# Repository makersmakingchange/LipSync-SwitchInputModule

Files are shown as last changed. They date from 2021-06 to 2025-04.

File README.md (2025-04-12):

# LipSync Switch Input Module

**As of 2024-Feb-08, this version of the LipSync is now obsolete and has been replaced by the [LipSync 4](https://github.com/makersmakingchange/LipSync).**
The LipSync 4 has 3 integrated switch ports for users who are unable to use sip and puff. Design files and documentation are maintained here for information only.

The LipSync Switch Input Module enables a user to use a [LipSync Classic](https://www.makersmakingchange.com/project/lipsync-classic/) with two assistive switches instead of the standard Sip and Puff mouthpiece. This can be a helpful adaptation for anyone who has difficulty forming their lips around the mouthpiece or generating the typical sips and puffs.

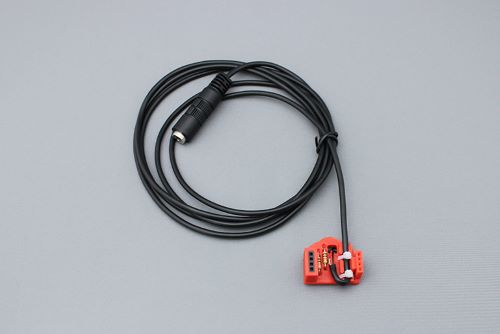
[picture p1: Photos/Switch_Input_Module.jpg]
LipSync Switch Input Module


## Getting Started

### 1. Order the Off-The-Shelf Components

The [Bill of Materials](/Documentation/Switch_Input_Module_BOM_v1.0.xlsx) lists all of the parts and components required to build the Switch Input Module. The electronic components may be available locally, but will probably need to be ordered online. Make sure you order the correct splitter.

### 2. Print the 3D Printed Circuit Board

Print the 3D Printed Circuit Board. The [file](/Build_Files/3D_Printing_Files/Switch_Input_3DPCB.stl) is in the [/Build_Files/3D_Printing_Files](/Build_Files/3D_Printing/) folder.

### 3. Disassemble the LipSync, Assemble and Install the Module, and Reassemble the LipSync 

Reference the [assembly guide](/Documentation/Switch_Input_Module_Assembly_Guide_v1.0.pdf) for the tools and steps required to complete each portion.

### 4. Attach an appropriate splitter and two suitable assistive switches.

Attach two momentary assistive switches.

## Files

### Documentation
| Document             | Version | Link                                                                                  |
|----------------------|---------|---------------------------------------------------------------------------------------|
| Design Rationale     | 1.0     | [Design_Rationale](/Documentation/Switch_Input_Module_Design_Rationale_v1.0.pdf) |
| Bill of Materials    | 1.0     | [BOM](/Documentation/Switch_Input_Module_BOM_v1.0.xlsx)                          |
| Assembly Guide       | 1.0     | [Assembly Guide](/Documentation/Switch_Input_Module_Assembly_Guide_v1.0.pdf)       |
| Quality Check Guide  | 1.0     | [Assembly Guide](/Documentation/Switch_Input_Module_Quality_Check_Guide_v1.0.pdf)       |
| User Quick Guide     | 1.0     | [Quick_Guide](/Documentation/Switch_Input_Module_User_Quick_Guide_v1.0.pdf)           |

### Design Files
 - [CAD Files](/Design_Files)

### Build Files
 - [3D Printing Files](/Build_Files/3D_Printing)
 - [V1.0 STL](/Build_Files/3D_Printing_Files/Switch_Input_3DPCB.stl)

## License
Copyright (c) 2022-2024 Neil Squire / Makers Making Change.

This repository describes Open Hardware:
 - Everything needed or used to design, make, test, or prepare the LipSync Switch Input Module is licensed under the [CERN 2.0 Weakly Reciprocal license (CERN-OHL-W v2) or later](https://cern.ch/cern-ohl ) .
 - Accompanying material such as instruction manuals, videos, and other copyrightable works that are useful but not necessary to design, make, test, or prepare the LipSync are published under a [Creative Commons Attribution-ShareAlike 4.0 license (CC BY-SA 4.0)](https://creativecommons.org/licenses/by-sa/4.0/) .

You may redistribute and modify this documentation and make products using it under the terms of the [CERN-OHL-W v2](https://cern.ch/cern-ohl).
This documentation is distributed WITHOUT ANY EXPRESS OR IMPLIED WARRANTY, INCLUDING OF MERCHANTABILITY, SATISFACTORY QUALITY AND FITNESS FOR A PARTICULAR PURPOSE.
Please see the CERN-OHL-W v2 for applicable conditions.

Source Location: https://github.com/makersmakingchange/LipSync-SwitchInputModule

## Attribution

The LipSync Switch Input Module was designed by Neil Squire Society / Makers Making Change. The initial development of a 3D printable LipSync was supported by the Google Impact Challenge: Disabilities grant from Google.org. Further development was supported through the Government of Canada's Innovation Science and Economic Development Assistive Technology Program. These and other funders have also enabled Neil Squire / Makers Making Change to deploy numerous LipSyncs to users at reduced cost.

### Contributors
Designers:
  - Derrick Andrews, Neil Squire Society / Makers Making Change.

----

<!-- ABOUT MMC START -->
## About Makers Making Change
[Makers Making Change Logo](https://www.makersmakingchange.com/)

Makers Making Change is a program of [Neil Squire](https://www.neilsquire.ca/), a Canadian non-profit that uses technology, knowledge, and passion to empower people with disabilities.

Makers Making Change leverages the capacity of community based Makers, Disability Professionals and Volunteers to develop and deliver affordable Open Source Assistive Technologies.

 - Website: [www.MakersMakingChange.com](https://www.makersmakingchange.com/)
 - GitHub: [makersmakingchange](https://github.com/makersmakingchange)
 - Bluesky: [@makersmakingchange.bsky.social](https://bsky.app/profile/makersmakingchange.bsky.social)
 - Instagram: [@makersmakingchange](https://www.instagram.com/makersmakingchange)
 - Facebook: [makersmakechange](https://www.facebook.com/makersmakechange)
 - LinkedIn: [Neil Squire Society](https://www.linkedin.com/company/neil-squire-society/)
 - Thingiverse: [makersmakingchange](https://www.thingiverse.com/makersmakingchange/about)
 - Printables: [MakersMakingChange](https://www.printables.com/@MakersMakingChange)

### Contact Us
For technical questions, to get involved, or to share your experience we encourage you to [visit our website](https://www.makersmakingchange.com/) or [contact us](https://www.makersmakingchange.com/s/contact).
<!-- ABOUT MMC END -->

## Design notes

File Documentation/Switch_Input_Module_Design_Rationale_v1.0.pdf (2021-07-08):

V1.0 | May 2021

## LipSync Switch Input Module

## Design Rationale

© 2021 by Neil Squire.
This work is licensed under the CC BY SA 4.0 License: http://creativecommons.org/licenses/by-sa/4.0
Files available at https://www.makersmakingchange.com/project/lipsync-switch-input-module/ | Page 1 of 7

## Introduction

The LipSync is a mouth operated joystick that emulates a computer mouse using a combination of lip movements and sip and puff breath control via a straw-like mouthpiece. Not all users are able to use the mouthpiece to input sip and puffs. The LipSync Switch Input Module enables a user to utilize two assistive switches in place of the pressure sensor to control the sip and puff functions. The Switch Adapted LipSync can be used with any assistive switches with a standard 3.5 mm plug.

## Commercial Options

Table 1 Commercial Options

Name | Vendor | Cost | Link
Jouse 3 | Compusult | CA$1,762. 61 | https://www.compusult.com
TetraMouse Model TMXA2 | TetraMouse | $449 | https://tetramouse.com
QuadJoy | QuadLIFE | $1,190.00 USD | https://quad.life/products-builder/p/style-02-56paj
The 'Sup’ | None (DIY Open Source) | $50 USD | https://www.instructables.com/The-Sup-a-Mouse-for-Quadriplegics-Low-Cost-and-Ope/

## Switch Adaption Choice

Existing commercial LipSync equivalents such as Tetramouse and QuadJoy already offer switch adaption options, so it seemed natural to offer an augmentation that would provide this benefit to our Lipsync users.

## Design Rationale

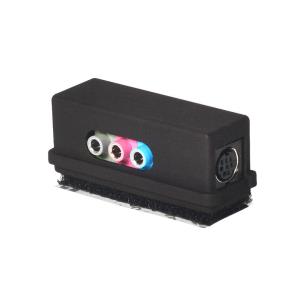
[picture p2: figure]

Files available at https://www.makersmakingchange.com/project/lipsync-switch-input-module/ | Page 2 of 7

### External Jack Interface

The inspiration for the Switch is the ‘External Jack Interface’ From QuadLIFE. It provides three 3.5 mm assistive jacks.

## Design Considerations

The goal for this version was to create a module that required minimal changes to the LipSync hardware and firmware.

To keep redesign of the LipSync to a bare minimum, the Switch Adapted LipSync module must fit the same connector and same general size footprint of the original pressure sensor daughterboard of the LipSync. Additionally, the Switch adaptation would need to mimic the functionality of this pressure sensor board, so that no (or minimal) firmware changes would be required to support this addition.

## Circuit Design

The choice was made to simulate the pressure sensor, so that no, or minimal, coding changes to the LipSync firmware would be required. The behavior of the pressure sensor is a straightforward transistor “totem pole” style output analogous to a voltage divider. The pressure sensor output voltage is half the supply voltage when no air pressure is applied through the sip and puff straw. Pumping air into the straw causes the voltage to drop and conversely, sipping air from the straw causes the voltage to increase. The decision was made to use two 100K resistors as a weak voltage divider. The switches would be placed in parallel with the two resistors. When a switch is activated it shorts out the resistor that it's in parallel with. Shorting out the lower resistor causes the voltage on the output to drop. This mimics ‘puff’ operation from the pressure sensor. Shorting out the upper resistor causes the output voltage to rise, which mimics ‘sip’ operation. While the two resistor circuit does all that’s required to satisfy the basics of mimicking a pressure sensor, the decision was made to add a second pair of resistors (10K value) to limit the current in the switch circuit. These resistors would ensure accidental wiring faults would not allow a short circuit of the Lip Sync USB power supply, and help absorb unwanted stray static charges.

## Design Rationale

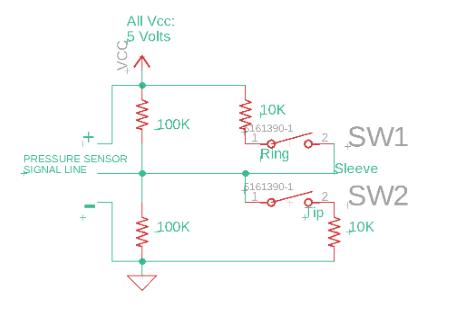
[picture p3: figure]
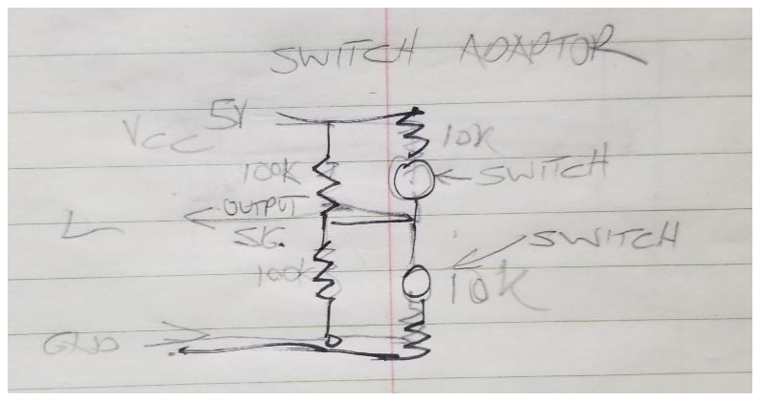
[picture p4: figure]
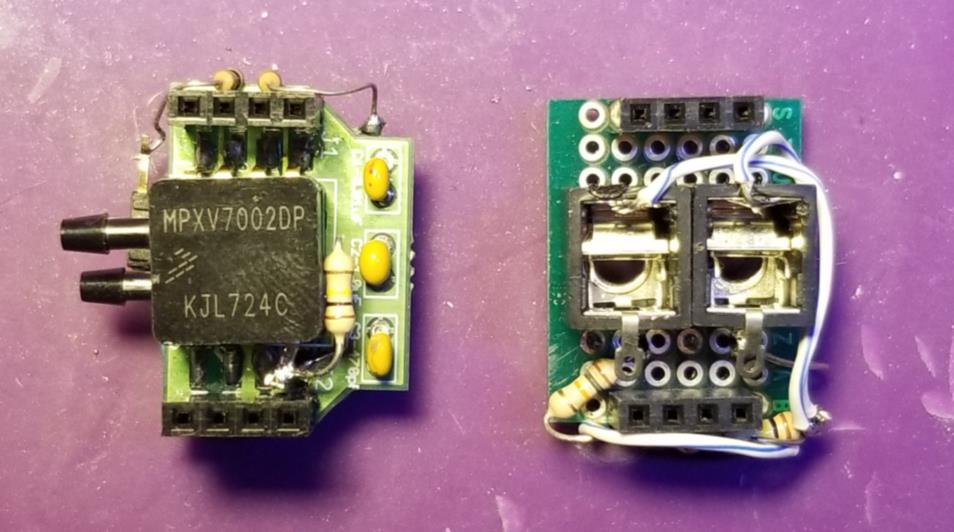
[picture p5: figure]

Files available at https://www.makersmakingchange.com/project/lipsync-switch-input-module/ | Page 3 of 7

Figure 1: Switch Modification Ideation

Figure 2: Early Prototypes

Figure 3: Early Prototypes: underside view

## Concept Testing

A pair of prototypes was constructed, on proto board, to test the basic premise of the circuit design. In the first prototype the original pressure sensor was left in place with a resistor added to protect it. then two switchers were soldered across this protected sensor output line. The LipSync was then powered up, and the joystick navigated to an

## Design Rationale

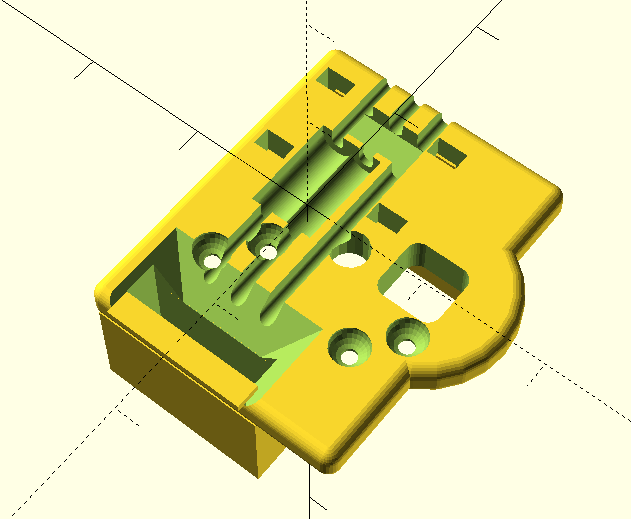
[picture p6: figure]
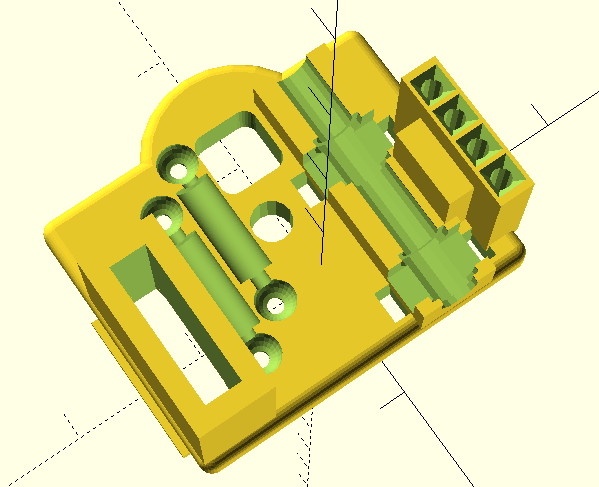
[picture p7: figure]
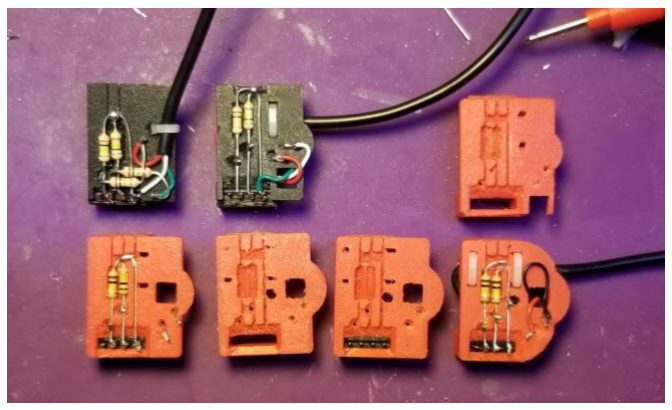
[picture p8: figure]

Files available at https://www.makersmakingchange.com/project/lipsync-switch-input-module/ | Page 4 of 7

icon desktop. Clicking on the lower button highlighted the icon, and clicking on the upper button, opened a menu on the desktop. All of these were expected behaviors for normal sip and puff operation on a Lip Sync.

## Version 1.1 Changes

This section will cover the changes and updates that was discussed in the previous section. The design changes focus more on improving the earlier design.

## 3D Printed Version

The usage of 3-D printing technology allows for low-cost production of the Switched LipSync with a minimum of parts. 3D also eliminates the need to cut or file potentially hazardous PCB material (fiberglass dust). Additionally, the 3-D print incorporates a circuit board, cable strain relief mounting and supporting header connector, all of which would have to be obtained separately, or custom built, if 3-D printing were not used.

## Design Rationale

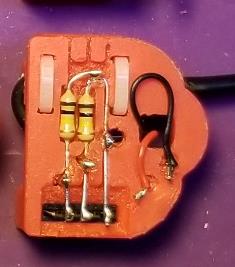
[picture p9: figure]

Files available at https://www.makersmakingchange.com/project/lipsync-switch-input-module/ | Page 5 of 7

## A Series of 3D Prototypes

During a meeting, the decision was made to construct the switch adapter using 3-D printing technology, as most makers now have access to this technology. 3-D printing offered a number of advantages. Firstly, it eliminated the need to purchase or fabricate a circuit board, or maintain inventory. Secondly, a header connector, and a cable strain relief, could be incorporated into the design, keeping costs low, by minimizing additional parts that would otherwise have to be sourced. To test the idea that a 3-D printed circuit board would work, a 3-D model was designed in OpenSCAD, a free, open source, code based modelling app. For simplicity, the first model incorporated all resistors on the top side of the circuit board. The result was functional, but crowded. The decision was then made to move the current limiting resistors to the underside of the design. With some feedback from our group of testers, we also reinforced the strain relief, slightly widened the header holes to allow for easier module installation, and added a central hole to keep the shield wire from coming into contact with the other wires. The final change was rounding the back end of the module so that it wouldn't touch the case of the LipSync.

## Switch Adapter Top Side

On the finalized switch adapter, you can see the main voltage divider resistors soldered to the header (lower black object) and the Tip and Ring wires (Black and red respectively). The Back end of the adaptor module is rounded to fit within the narrower back end of the LipSync case. The bulky ends of the cable ties have been relegated to the bottom side to avoid snagging.

## Design Rationale

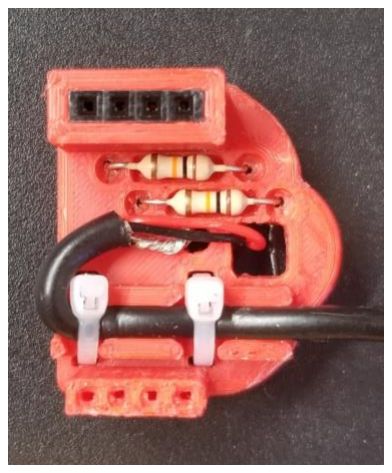
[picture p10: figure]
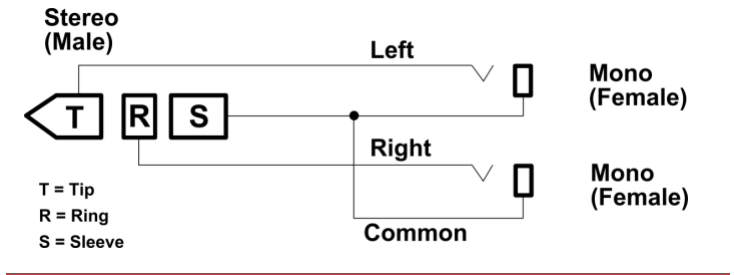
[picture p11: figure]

Files available at https://www.makersmakingchange.com/project/lipsync-switch-input-module/ | Page 6 of 7

## Switch Input Module Bottom

Figure 1: Bottom of Switch Input Module

The bottom side of the switch adapter shows the connector side of the inserted female header (top of image) and the two current limiting resistors (10K). The female 3.5mm jack stereo cable enters the adaptor (bottom right) where it is held firmly in place by two small cable ties. From there, the cable loops up and to the right, where the sleeve wire emerges from the cable, and enters the small hole, to connect to the center of the voltage divider. The Tip and Ring wires (Black and red respectively) enter the larger square hole, to connect with the current limiting resistors, where their wires emerge on the top side of the board.

## Breakout Cable

3.5 mm TRSM to Dual 3.5 mm TSF Breakout Cable ($16.46, e.g. Amazon) (https://www.amazon.ca/gp/product/B000068O5H)

There are two types of 3.5 mm splitters that appear very similar. The type required for this device separates the left and right channels into mono connections. This is different than the type that is more commonly available and often used for sharing sound between two users.

## Design Rationale

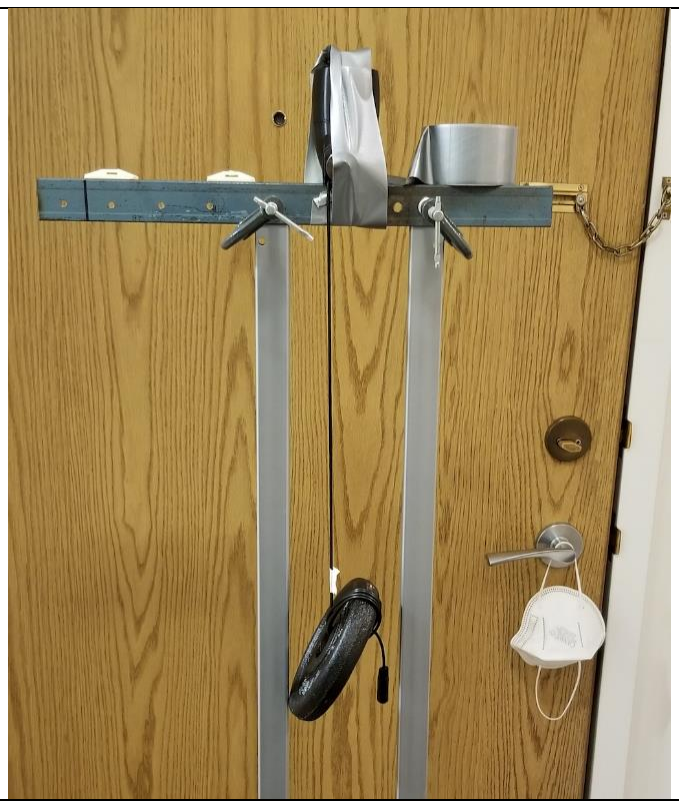
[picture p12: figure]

Files available at https://www.makersmakingchange.com/project/lipsync-switch-input-module/ | Page 7 of 7

## Testing

### Cord Testing

The Switch Input Module Cord was tested for mechanical strength. Specifically, the cord was tested to ensure the mounting was robust enough to withstand being pulled in ways that might occur during real world use.

Initially, we chose to secure the LipSync cord and drop the LipSync using its own weight. The cord mounting survived up to a 120 cm drop before scuffing to the cord was observed. As a final “torture test”, we taped the LipSync to a metal support frame, and attached a 2.2 Kg (5lb) mass to the cord. This was dropped 30 cm, causing the header pins on the LipSync to bend, but the Switch Adaptor and cord remained intact and functional. This was considered satisfactory, as it suggested the adaptor and cord were more rugged than the LipSync itself.

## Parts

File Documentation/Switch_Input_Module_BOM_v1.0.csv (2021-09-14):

Device: Switch Input Module |  | Total Cost | Total Print time (hr) | Total filament (g)
Version: V1.0 | Date Created: 6/5/2021 | $19.47 | 0.57 | 2.5
Commercial Parts: | Does not include component shipping.
Part type (Electrical, Mechanical, Sanitization, etc) | Part | Quantity Needed | Pkg Quantity | Price per package | Price per Unit | Price for qty needed | Link | Alternative
Electrical | 4-Position Straight Female Through-Hole Header | 1 | 1 | $0.63 | $0.63 | $0.63 | http://www.digikey.ca/product-detail/en/sullins-connector-solutions/PPPC041LFBN-RC/S7037-ND
Electrical | 10K Ohm 1/4W Mini Axial Through-Hole Resistor | 2 | 1 | $0.14 | $0.14 | $0.28 | https://www.digikey.ca/product-detail/en/stackpole-electronics-inc/CFM14JT10K0/S10KQCT-ND/
Electrical | 100K Ohm 1/4W Mini Axial Through-Hole Resistor | 2 | 1 | $0.14 | $0.14 | $0.28 | https://www.digikey.ca/en/products/detail/stackpole-electronics-inc/CFM14JT100K/1742059?s=N4IgTCBcDaIMIDECyBGALAKQCooAy4GkQBdAXyA
Mechanical | Cable Tie | 2 | 1 | $0.14 | $0.14 | $0.28 | https://www.mouser.ca/ProductDetail/Panduit/PLT6SM-M
Electrical | 3.5 mm Female Stero Cable - 6ft | 1 | 1 | $1.48 | $1.48 | 1.48 | https://www.primecables.ca/p-306304-cab-audio-ex-mf-6ft-35mm-stereo-plugjack-mf-extension-cable-6ft-primecables
Electrical | 3.5 mm Stereo Breakout cable | 1 | 1 | $16.46 | $16.46 | 16.46 | https://www.amazon.ca/gp/product/B000068O5H/ref=ppx_yo_dt_b_asin_title_o00_s00?ie=UTF8&psc=1
3D Printed Parts ESTIMATED PRICING USING 1KG ROLL COST: | $25.00
Part File Name | Description | Quantity Needed | TOTAL Mass (g) | Estimated Price | Print Time (Min) | Link
Switch_Input_Module.stl | Switch Input Module 3D Printed Circuit Board | 1 | 2.5 | $0.06 | 34
 |  |  |  | $-
 |  |  |  | $-
 |  |  |  | $-
 |  |  |  | $-
 |  |  | Total Print Cost: | $0.06
Tools for Assembly
solder
soldering kit
wire strippers
side cutters
pliers
(hobby knife / scalpel)
Alternatives (if there are other sources for some parts link them below)
Part and description | Link
3.5mm Female Stero Cable - 6ft For US SHIPPING | https://www.allelectronics.com/item/cb-333/6-3.5mm-m-f-extension-cord/1.html
Cable Ties | Can also be sourced from dollar store / home depot/ local hardware shop

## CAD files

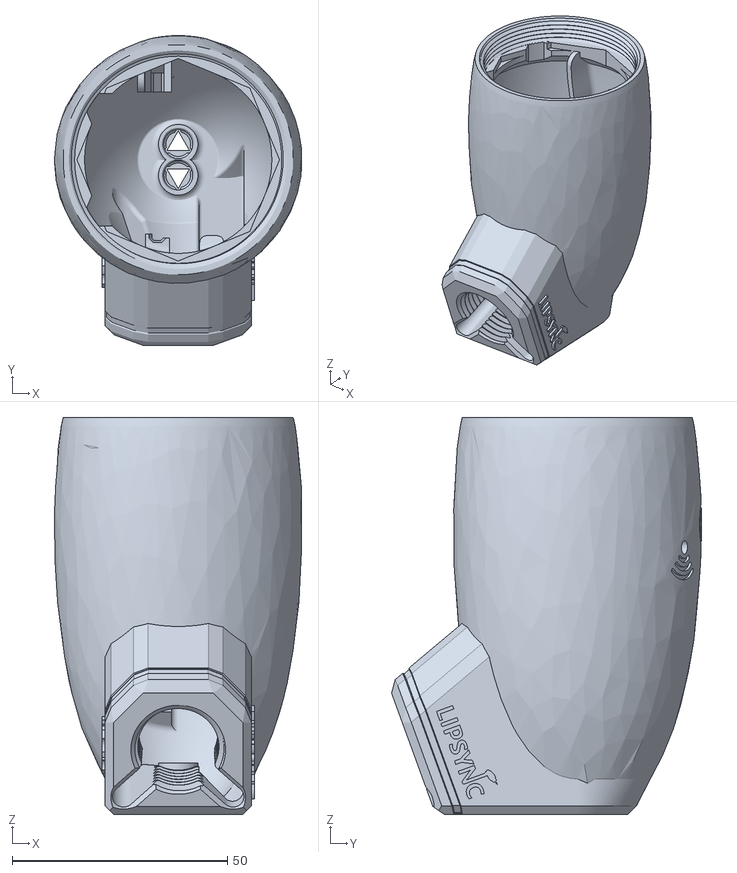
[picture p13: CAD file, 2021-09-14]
Build_Files/3D_Printing_Files/LipSync_Rear_Housing.STL
57.5 x 72.0 x 92.2

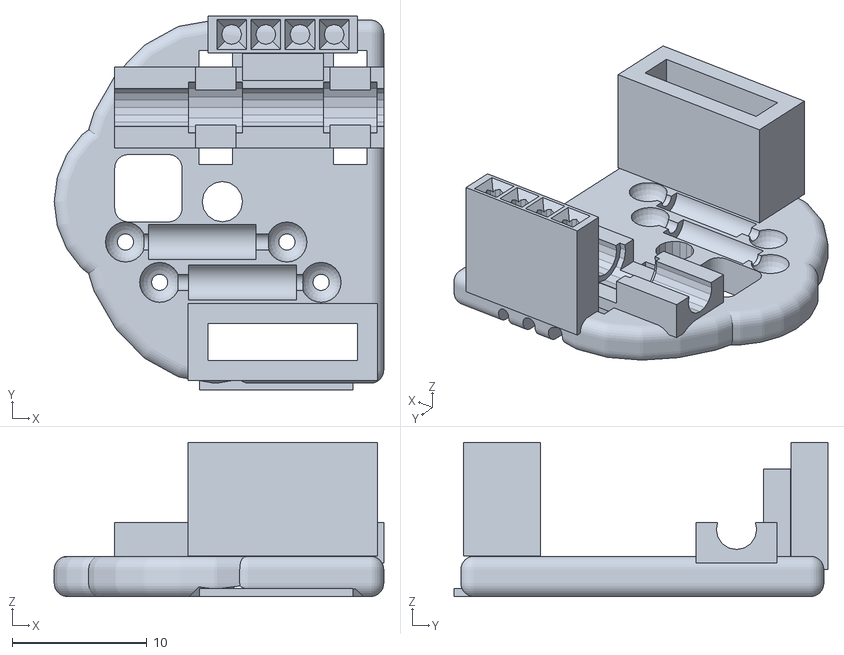
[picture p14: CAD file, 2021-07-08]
Build_Files/3D_Printing_Files/Switch_Input_3DPCB.stl
24.5 x 27.8 x 11.5

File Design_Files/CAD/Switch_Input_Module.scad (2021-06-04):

// Switch Input Module for LipSync
// Makers Making Change
// V1.0
pinSpacing=2.54; //.100" spacing
boardWidth=21;
boardDepth=27.0;
boardHeight=3;//1.59;
headerDepth=2.54+.2;
headerHeight=8.46;
headerWidth=10.7+.4;
//headerPinWidth=.65+.2;//square side
headerPinWidth=.88+.6;//diameter increased twice was.4
headerPinPlugHeight=6;
headerPinTotalHeight=11.2;
ballDia=3; //for ballVia 


//pseudo header
difference(){
translate ([0,pinSpacing*4.5,headerHeight/2+boardHeight-.5])cube([headerWidth,headerDepth,headerHeight+1],center=true) ;
translate ([0,pinSpacing*4.5,headerPinTotalHeight/2-(boardHeight/2)])ArrayCentItems(4,1,pinSpacing,pinSpacing)cylinder (d=headerPinWidth,h=headerPinTotalHeight+5,center=true,$fn=12) ;
translate ([0,pinSpacing*4.5,11.5])ArrayCentItems(4,1,pinSpacing,pinSpacing)rotate([180,0, 45])cylinder (h=1.6,r1=1.6,r2=0,$fn=4);//(makes pyramid)
}//diff

translate ([0,9,7/2+boardHeight-.5])cube([6,2,7],center=true) ;  //brace
translate ([-6.2,-15,0])cube([11.4,2,.6],center=false) ;  //support material
//translate ([0,pinSpacing*4.5,headerPinTotalHeight/2-(boardHeight/2)])ArrayCentItems(4,1,pinSpacing,pinSpacing)cube([headerPinWidth,headerPinWidth,headerPinTotalHeight],center=true) ;
difference(){
union(){
translate ([0,pinSpacing*-4.5,headerHeight/2+boardHeight])cube([headerWidth+3,headerDepth+3,headerHeight],center=true) ;
translate ([-3+5,-1,boardHeight/2])roundedCube (boardWidth-10,boardDepth,boardHeight,1);//pseudo PCB board
translate ([-5,-1,boardHeight/2])minkowski(){//rounded body
scale([.75,1,1])cylinder(h = boardHeight-2, d = boardDepth-2, center = true,$fn=24);
sphere(r=1,center=true,$fn=30);
}  //end mink
translate ([-10,-1,boardHeight/2])minkowski(){//"tail"
cylinder(h = boardHeight-2, d = 12, center = true,$fn=24);
sphere(r=1,center=true,$fn=30);
}  //end mink
}//end union	
//cube([boardWidth,boardDepth,boardHeight],center=true) ;//pseudo PCB board
//roundedCube (boardWidth,boardDepth,boardHeight,1)


translate ([0,pinSpacing*-4.5,headerHeight/2+boardHeight])cube([headerWidth,headerDepth,headerHeight+10],center=true) ;
translate ([-.5, 5-3, 1])rotate([0,180, 0])resistorSlot (8,2.6,1.2,30);//5v 100k resistor slot
translate ([pinSpacing*1-.5, 5-3, 1])rotate([0,180, 0])resistorSlot (8,2.6,1,30);//0v 100k resistor slot




translate ([pinSpacing*-1-.5, 5-3, 1])rotate([0,180, 0])resistorSlot (0,3,1.2,30);// resistor wire
translate ([.3, -1-3, boardHeight/2])ballVia (boardHeight,1.2,ballDia);//5v 100K/10k resistor hole
translate ([pinSpacing*1+.3, -4-3, boardHeight/2])ballVia (boardHeight,1.2,ballDia);//0v 100k/10k resistor hole
translate ([-6, -1-3, 3])rotate([0,0, 90])resistorSlot (8,2.6,1.2,8+4);//0v 10k resistor slot (underside)
translate ([-3, -4-3, 3])rotate([0,0, 90])resistorSlot (8,2.6,1.2,8+4);//0v 10k resistor slot (underside)

translate ([.3-12, -1-3, boardHeight/2])ballVia (boardHeight,1.2,ballDia);//5v 10k resistor hole
translate ([pinSpacing*1+.3-12, -4-3, boardHeight/2])ballVia (boardHeight,1.2,ballDia);//0v 10k resistor hole


translate ([-.5,8,0])cube([5.5,3,3.3], center = true); //resistor solder clearance


translate ([-10,0,2.5])minkowski(){
cube([3,3,6], center = true); //cable thru hole
sphere(r=1,center=true,$fn=30);
}  //end mink

translate ([-5,2.5,2.5])cube([2.5,1.5,5], center = true); //cable tie  hole
translate ([-5,9.5,2.5])cube([2.5,1.5,5], center = true); //cable tie  hole
translate ([5,2.5,2.5])cube([2.5,1.5,5], center = true); //2nd cable tie  hole
translate ([5,9.5,2.5])cube([2.5,1.5,5], center = true); //2nd cable tie  hole

translate ([-4.5,-1,2.5])cylinder(d=3,h=15.1,center=true,$fn=16);//braid soldering hole
//translate ([0,-10,0])rotate([-30,0, 0])cube([11,5,3], center = true);//old header solder joint clearance

translate ([-3,-11,-1])hull() {
    translate([5,0,0]) rotate([0,0, 45])cylinder (h=5,r1=7,r2=0,$fn=4);//(makes pyramid)
    rotate([0,0, 45])cylinder (h=5,r1=7,r2=0,$fn=4);//(makes pyramid)
}//hull

}//end diff



//translate ([0,pinSpacing*-4.5,headerPinTotalHeight/2-(boardHeight/2)])ArrayCentItems(4,1,pinSpacing,pinSpacing)cube([headerPinWidth,headerPinWidth,headerPinTotalHeight],center=true) ;//***temporary
translate ([-5,6,4])rotate([0,0, 90])cableGrip (); // *** turned off 
//! ! ! ! !  ! ! !!!!!!!!!!!!!!  testing !!!!!!!!!!!!!!!!!!!!!!!!!

module cableGrip ()
difference(){
translate ([0, -2.5,0])cube([6,20,3], center = true);
translate ([0, -2.5,1])rotate([90,0, 0])cylinder(d=3,h=20.1,center=true,$fn=16); //cable slot
translate ([0, 0,1])rotate([90,0, 0])cylinder(d=4,h=4,center=true,$fn=16);// cable snagger
translate ([0, 0,2])rotate([90,0, 0])cube([6,5,3], center = true);//cinching slot in cable snagger
translate ([0, -10,1])rotate([90,0, 0])cylinder(d=4,h=4,center=true,$fn=16);// 2nd cable snagger
translate ([0, -10,2])rotate([90,0, 0])cube([6,5,3], center = true);//2nd cinching slot in cable snagger	
}//end module cable grip




module resistorSlot (compLeng,compDiam,wireDiam,wireLeng)
//example use:   resistorSlot (8,2.6,1,25);  //creates standard 1/4 watt resistor slot
{
	translate ([0, 0,compDiam/4])cube([compDiam,compLeng,compDiam/2], center = true);//component channel
rotate([90,0, 0]) cylinder(d=compDiam,h=compLeng,center=true,$fn=100);//component bed
translate ([0, 0,compDiam/4])cube([wireDiam,wireLeng,compDiam/2], center = true);//wire channel
rotate([90,0, 0]) cylinder(d=wireDiam,h=wireLeng,center=true,$fn=100);	//rounded wire bed
} //end resistor slot



module ballVia (pcbThick,boreDiam,sphereDiam)
//make sure sphereDiam is always less than board thickness!!!
{
//sphere(d = boreDiam,$fn=24);
//cylinder(D=boreDiam,h=pcbThick-sphereDiam,$fn=100);
	cylinder(h = pcbThick, d = boreDiam, center = true,$fn=24);
	translate ([0,0,pcbThick/2])sphere(d = sphereDiam,$fn=24);
	translate ([0,0,pcbThick/-2])sphere(d = sphereDiam,$fn=24);
	}//end module ballVia
	
	

module ArrayCentItems(xCount,yCount,itemGapX,itemGapY)
{
for (x = [1:xCount]){
for (y = [1:yCount]){
translate([x*itemGapX-(xCount+1)*itemGapX/2,y*itemGapY-(yCount+1)*itemGapY/2,0])
children();
}//for y
}//for x
}//end module

module CircleItems(n,r,myRot)
{
segment=360 / n;
for (i=[1:n])
{
rotate([0, 0, segment*i+myRot])
translate ([r,0,0])
children();
}//for
}//module


module roundedCube (myBoxWidth,myBoxDepth,myBoxHeight,minkRadius)
//** Same as regular cube, but with rounded sides and bottom
//** maintains proper 'cube' dimensions due to compensation for object expansion 
//** that normally occurs while using Minkowski operations in OpenSCAD)
{
union()
{

minkowski(){
cube([myBoxWidth-minkRadius*2,myBoxDepth-minkRadius*2,myBoxHeight-minkRadius*2], center = true);//Main plate   original cube([90,testSize8,8.5]
sphere(r=minkRadius,center=true,$fn=30);
}  //end mink


}//end union
}//end module roundedCube

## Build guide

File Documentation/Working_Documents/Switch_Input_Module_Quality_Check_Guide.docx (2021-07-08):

# Quality Check Guide

# Device: Switch Input Module

Version: V1.0 Date: 5/12/2021

## Introduction:

When the switch input module build has been completed is important to run through the following quick checks to mitigate any future component failures. This document contains the common checks that makers can do to ensure that their build is of an acceptable quality.

Fig 1:

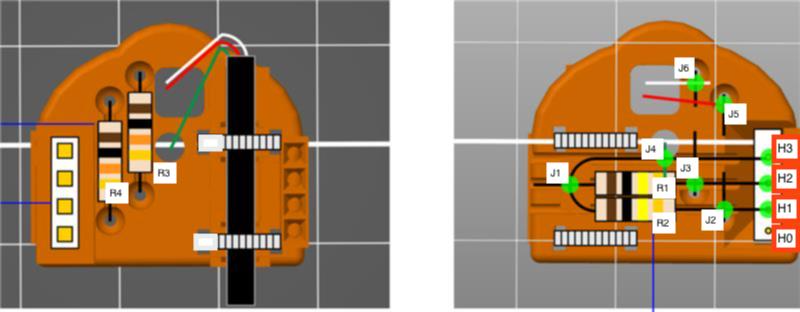
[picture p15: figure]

## Quality Checks:

Below is the set of quality checks to do after the build is complete:

3D Printed Housing:

- After printing the circuit housing be sure to check the part for any obvious flaws, such as the following:
  - Stringing
  - Extra filament left over from print such as support or small globs
  - Gaps in the print causing structural errors
  - Messy print quality resulting in a brittle component
- All of the unwanted filament has been removed. Such as some residue from a brim or any support, use a blade or plyers to scrape/pull away any of this excess carefully.

Solder Points:

- Ensure all solder points are smooth and shiny. Make sure they don’t blob together with other solder joints, which can form short circuits.

Wires:

- The wires don’t have stray strands sticking out, and touching component leads, or other wires.
- Wire length is not excessive, otherwise, the adaptor may not fit into the LipSync shell.

Assembly:

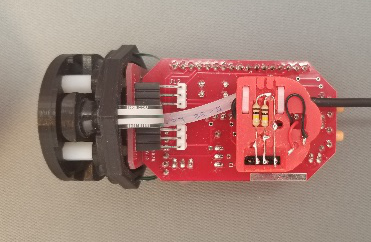
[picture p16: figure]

- The module is orientated correctly on the LipSync board as shown in the instructions.
- The connection is secure, making sure the module has been placed on all the way.
- The strain relief precautions have been added to the model such as adding the zip ties as explained in the instructions.

Circuit:

- Confirm that the appropriate connections have been made by reviewing the instructions and reviewing the circuit diagram below. If you are unsure if the component is wired correctly, there are two different tests one can do, described below as well.

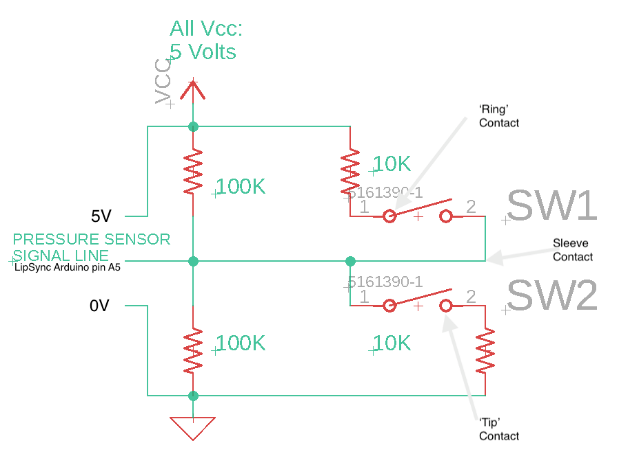
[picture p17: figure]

Testing the circuit electrically:

If you have access to a multimeter, you can test by setting the meter to the 1M (1 mega ohm) ohm range. Note that if your multimeter is auto ranging, then you’ll only need place it on the ohms (resistance) setting. Strip the wire end of the leftover male cable end, so you have the conductive metal strands exposed ‘tip', 'ring’ and ‘sleeve’ wires. Insert the male cable end into the Switch Module’s female jack. Make sure the LipSync is unpowered at this point. Using the meter, measure the resistance between the ‘tip’ and ‘ring’ wires (Tip is usually white, though may be black. Ring is almost always red). You should get a reading of 220 K ohms (within a range of 10%). This loop test confirms the overall integrity of the circuit, with the exception of power. To ensure the circuit is powered, set the multimeter to DC volts (use 5 or ten volt range, if not auto ranging). Turn on the LipSync, and measure the voltage between the same ‘tip’ and ‘ring’ contact points you measured in the previous test. You should see a reading of 5V.

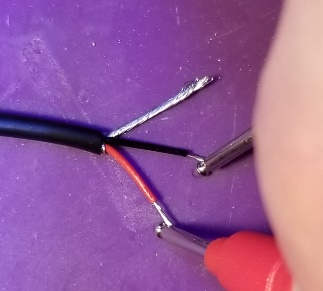
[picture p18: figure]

If you don’t' have access to a multimeter, you can test using a standard 3-5mm red LED, attaching the positive lead (usually the longest) to the ‘ring’ contact (usually red wire) and the negative lead to the ‘tip’ contact (usually white, though may be black). The Switch Adaptor will need to be installed in the LipSync, and turned on. If the LED turns on, though it may appear to be a bit dimmer than normal.

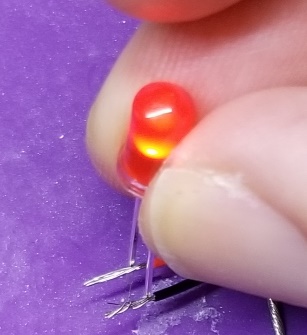
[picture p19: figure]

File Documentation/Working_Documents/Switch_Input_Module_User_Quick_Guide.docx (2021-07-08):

# User Quick Guide

# Device: Switch Input Module

Version: 1.0 Date: 05/17/2021

## Introduction:

The LipSync is a sip and puff joystick that emulates a computer mouse. When the switch input module is added to a LipSync it allows switches to be used in place of regular the sip and puff functionality. This means that left and right mouse clicks can be controlled by switch interfaces. This adaptation is suitable for LipSync users who have low lung capacity or those who can’t form their lips around the joystick mouthpiece.

## Features:

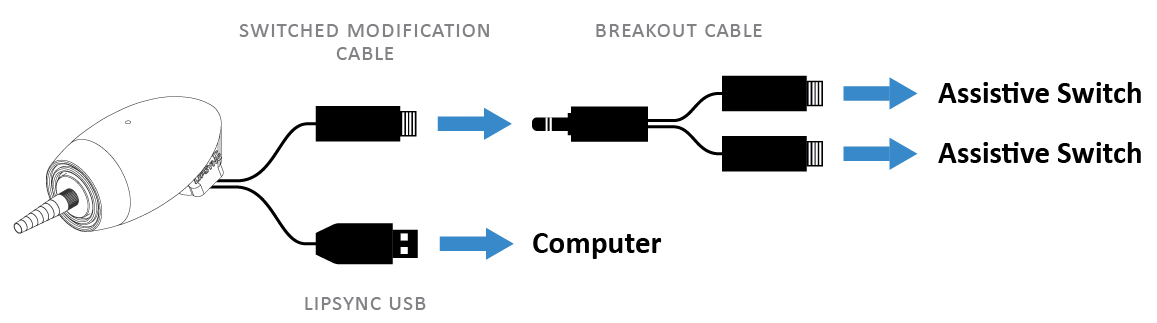
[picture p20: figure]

The switch module features a USB cable and a break-out cable. The USB cable is used to connect the LipSync to the desired device, and the break-out cables allow for two switches to be connected to control sip and puff.

## Device Setup:

If this is a new LipSync: The LipSync has its own set up process that must be referred to first. The LipSync start-up guide can be found here: https://github.com/makersmakingchange/LipSync/blob/master/LipSync_Startup_Guide.pdf

Once the LipSync has been calibrated and setup, the switch module setup can now begin:

1) Connect the LipSync USB to an electronic device (except on iOS devices) with a USB adapter if applicable) or a power bank.

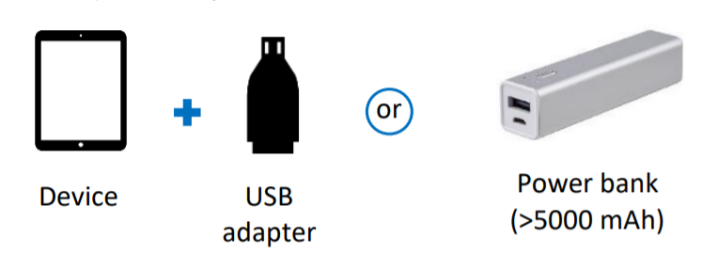
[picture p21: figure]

2) After plugging the LipSync to a power source, initialization will begin automatically. Do not touch the LipSync while the LED blinks red and green. Wait until the LED stops flashing before moving the mouthpiece. Initialization will occur every time the LipSync is plugged into a device.

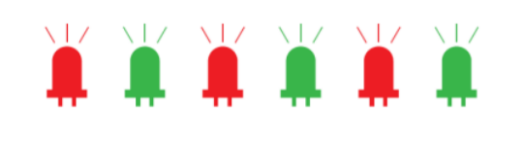
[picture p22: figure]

3) Insert the male end of the breakout cable into the female end of the Switched LipSync Modification cable.

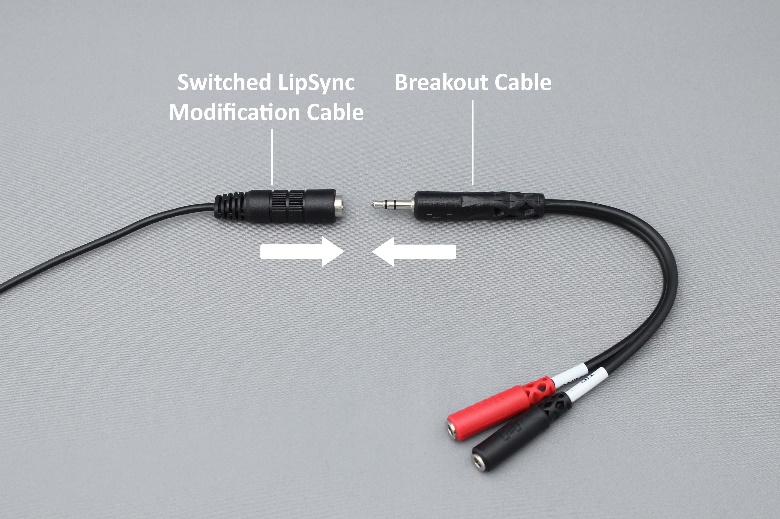
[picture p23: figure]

4) Insert the first assistive switch into the ‘Left Click’ connector of the breakout cable labelled “TIP”. This female cable end is usually black or white.

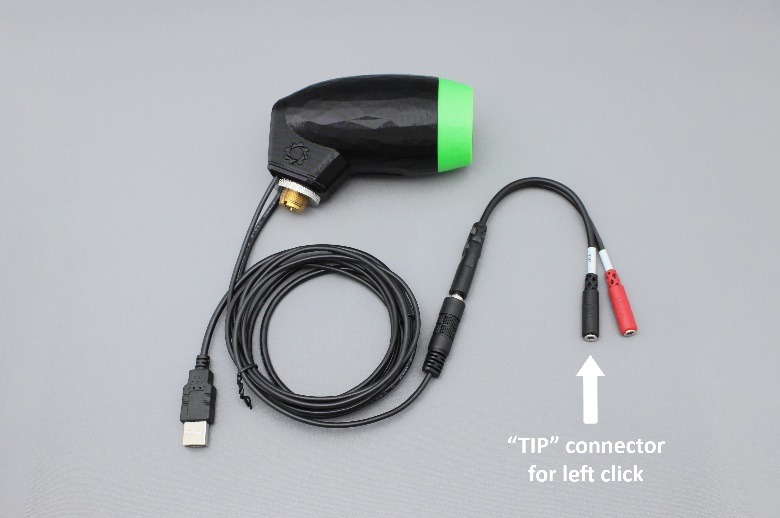
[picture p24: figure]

5) Insert the second assistive switch into the ‘Right Click’ connector of the breakout cable labelled “RING”. This female cable end is usually red.

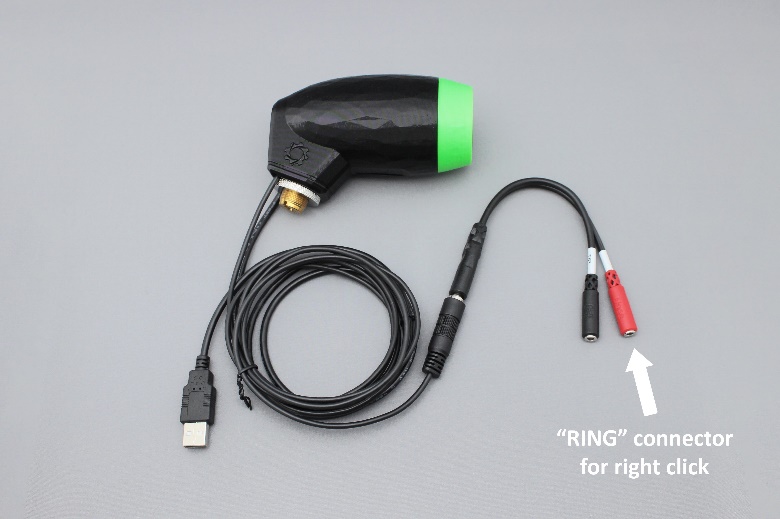
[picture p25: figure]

6) The Switched LipSync should look like this with two assistive switches connected:

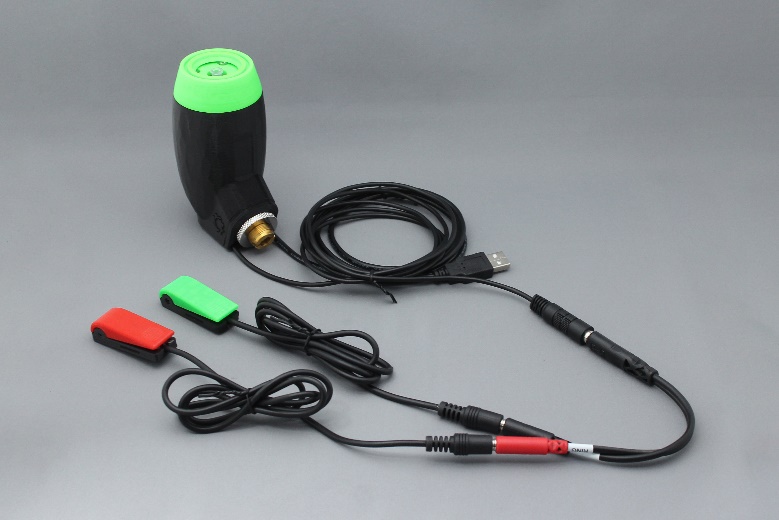
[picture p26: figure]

## Usage:

Ensure the LipSync USB is connected to a phone, tablet, or computer; and 2 switches are connected to the LipSync breakout cable. After that the following can be used as such:

Device Action | Action Time | Function
Moving the mouthpiece joystick | <1 second | Moves mouse cursor around the screen
Activating the “TIP” connected switch | < 1 second | Left mouse click
Activating the “TIP” connected switch twice | < 1 second each | Double left click
Activating the “RING” connected switch | < 1 second | Right mouse click
Activating the “TIP” connected Switch | 3 seconds ¹ | Toggle
Activating the “RING” connected Switch | 3 seconds ² | Scrolling
Cursor home reset | 5 seconds | Helps to alleviate mouse cursor drift

¹ The red LED will stay on at all times in Toggle mode. Deactivate mode by doing a 1 second sip or puff.
² The green LED will stay on at all times in Scrolling mode. Deactivate mode by doing a 1 second sip or puff.

## Compatibility

Any assistive switch that uses a 3.5 mm mono cable or has a built in 3.5 mm mono cable jack. Wireless switches will not be able to connect to this switch module.

## Specifications

Mass: Approx. 25 grams (Switch Input module with cable, without adaptor cable or switches).

Dimensions: 25 x 27 x 11 mm

## Cleaning

Only the cable will need to be cleaned periodically, as the Switch Module resides internally within the LipSync, and should not normally require cleaning. However, both the cable and module are cleanable with 90% purity (or greater) isopropyl alcohol.

© 2021 by Neil Squire. This work is licensed under the CC BY SA 4.0 License: http://creativecommons.org/licenses/by-sa/4.0 PAGE 1 OF 1 Design files available at https://github.com/makersmakingchange/LipSyncSwitchInputModule

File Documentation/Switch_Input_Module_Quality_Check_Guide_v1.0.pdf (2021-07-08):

V1.0 | June 2021

## LipSync Switch Input Module

## QUALITY CHECK QUIDE

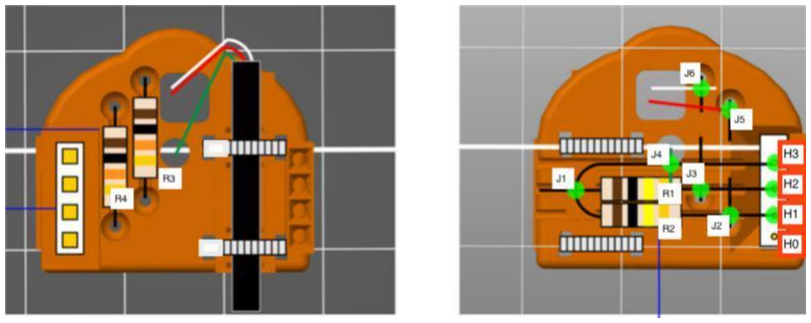
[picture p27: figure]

© 2021 by Makers Making Change. This work is licensed under the CC BY SA 4.0 License: http://creativecommons.org/licenses/by-sa/4.0
Files available at https://www.makersmakingchange.com/project/lipsync-switch-input-module/ | Page 1 of 3

## Introduction

When the switch input module build has been completed is important to run through the following quick checks to mitigate any future component failures. This document contains the common checks that makers can do to ensure that their build is of an acceptable quality.

Fig 1:

## Quality Checks

Below is the set of quality checks to do after the build is complete:

3D Printed Housing:

❑ After printing the circuit housing be sure to check the part for any obvious flaws, such as the following:
- Stringing
- Extra filament left over from print such as support or small globs
- Gaps in the print causing structural errors
- Messy print quality resulting in a brittle component
❑ All of the unwanted filament has been removed. Such as some residue from a brim or any support, use a blade or plyers to scrape/pull away any of this excess carefully.

Solder Points:

❑ Ensure all solder points are smooth and shiny. Make sure they don’t blob together with other solder joints, which can form short circuits.

Wires:

❑ The wires don’t have stray strands sticking out, and touching component leads, or other wires. ❑ Wire length is not excessive, otherwise, the adaptor may not fit into the LipSync shell.

## QUALITY CHECK QUIDE

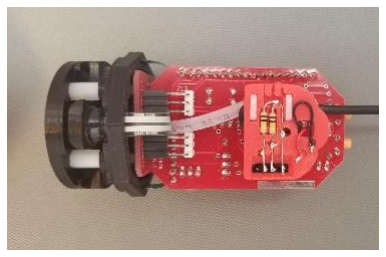
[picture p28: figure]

Files available at https://www.makersmakingchange.com/project/lipsync-switch-input-module/ | Page 2 of 3

Assembly:

❑ The module is orientated correctly on the LipSync board as shown in the instructions.
❑ The connection is secure, making sure the module has been placed on all the way.
❑ The strain relief precautions have been added to the model such as adding the zip ties as explained in the instructions.

Circuit:

❑ Confirm that the appropriate connections have been made by reviewing the instructions and reviewing the circuit diagram below. If you are unsure if the component is wired correctly, there are two different tests one can do, described below as well.

## QUALITY CHECK QUIDE

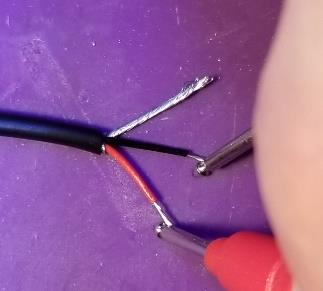
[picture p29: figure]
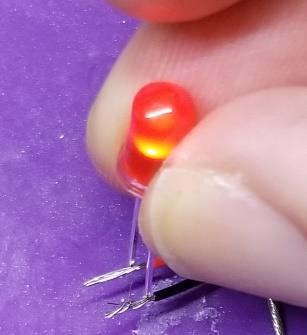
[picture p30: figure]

Files available at https://www.makersmakingchange.com/project/lipsync-switch-input-module/ | Page 3 of 3

Testing the circuit electrically:

If you have access to a multimeter, you can test by setting the meter to the 1 M (1 mega ohm) ohm range. Note that if your multimeter is auto ranging, then you’ll only need place it on the ohms (resistance) setting. Strip the wire end of the leftover male cable end, so you have the conductive metal strands exposed ‘tip', 'ring’ and ‘sleeve’ wires. Insert the male cable end into the Switch Module’s female jack. Make sure the LipSync is unpowered at this point. Using the meter, measure the resistance between the ‘tip’ and ‘ring’ wires (Tip is usually white, though may be black. Ring is almost always red). You should get a reading of 220 K ohms (within a range of 10%). This loop test confirms the overall integrity of the circuit, with the exception of power. To ensure the circuit is powered, set the multimeter to DC volts (use 5 or 10 V range, if not auto ranging). Turn on the LipSync, and measure the voltage between the same ‘tip’ and ‘ring’ contact points you measured in the previous test. You should see a reading of 5V.

If you don’t' have access to a multimeter, you can test using a standard 3-5 mm red LED, attaching the positive lead (usually the longest) to the ‘ring’ contact (usually red wire) and the negative lead to the ‘tip’ contact (usually white, though may be black). The Switch Adaptor will need to be installed in the LipSync, and turned on. If the LED turns on, though it may appear to be a bit dimmer than normal.

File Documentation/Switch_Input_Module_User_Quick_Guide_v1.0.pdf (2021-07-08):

V1.0 | June 2021

## LipSync Switch Input Module

## USER QUICK GUIDE

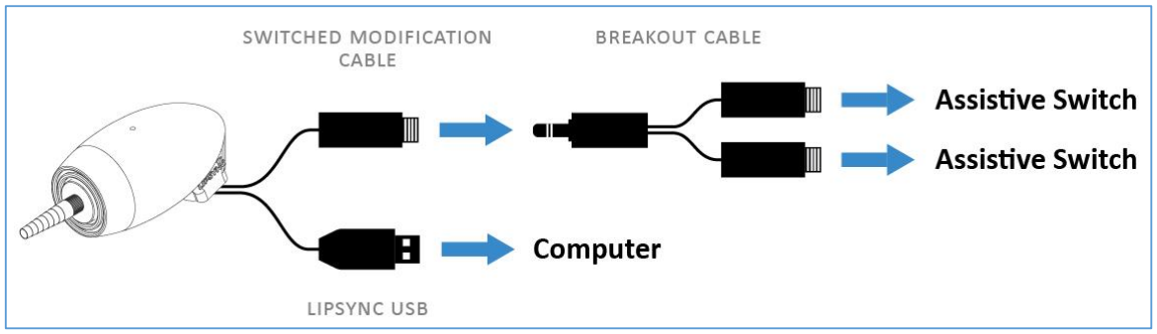
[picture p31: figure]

© 2021 by Neil Squire. (https://neilsquire.ca/)
This work is licensed under the CC BY SA 4.0 License: http://creativecommons.org/licenses/by-sa/4.0
Files available at https://www.makersmakingchange.com/project/lipsync-switch-input-module/ | Page 1 of 3

## Introduction

The LipSync Switch Input Module enables users to use assistive switches in place of the standard sip and puff input of the LipSync. This means that left and right mouse clicks or can be controlled by activating a switch. This adaptation may be helpful for LipSync users who have difficulty applying sips and puffs to the standard LipSync.

## Features

The Switch Input Module adds a 3.5 mm stereo cable with a breakout splitter cable to the LipSync enclosure. Two assistive switches with 3.5 mm mono cables can be attached to control the sip and puff functions of the LipSync.

## Usage

Ensure the LipSync USB is connected to a phone, tablet, or computer and 2 switches are connected to the LipSync breakout cable. After that the following can be used as such:

Device Action | Action Time | Function
Moving the mouthpiece joystick | <1 second | Moves cursor around the screen
Activating the “TIP” Switch | < 1 second | Left click
Activating the “TIP” Switch twice | < 1 second each | Double left click
Activating the “RING” switch | < 1 second | Right click
Activating the “TIP” Switch | 3 seconds ¹ | Drag Mode
Activating the “RING” Switch | 3 seconds ² | Scroll Mode
Activating the “TIP” Switch | 5 seconds | Reset joystick center position.
1 The red LED will stay on at all times in Drag mode. Deactivate mode by doing a 1 second sip or puff.
2 The green LED will stay on at all times in Scroll mode. Deactivate mode by doing a 1 second sip or puff.

## Compatibility

Any assistive switch that uses a 3.5 mm mono cable or has a built in 3.5 mm mono cable jack. The Switch Input Module is not compatible with Wireless switches.

## USER QUICK GUIDE

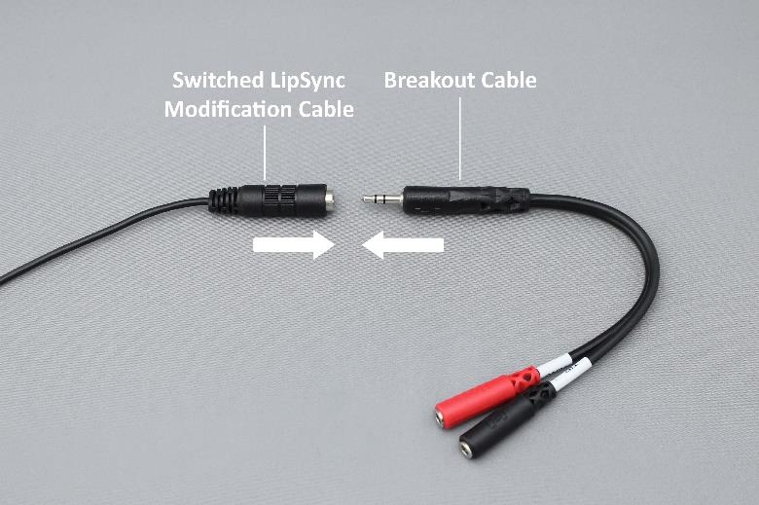
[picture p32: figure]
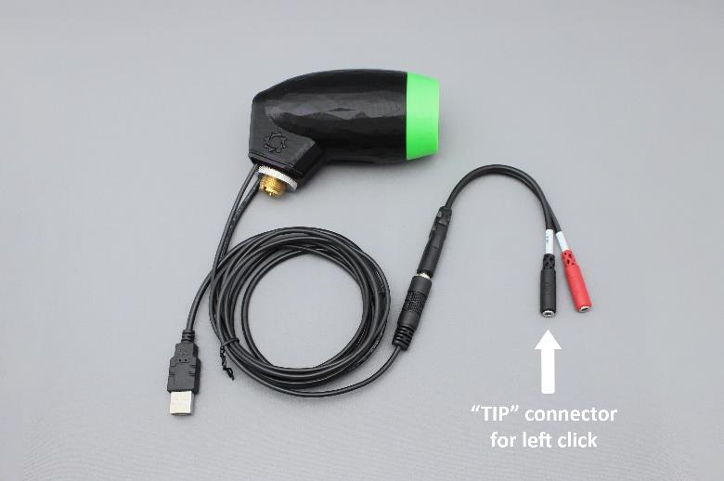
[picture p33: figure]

Files available at https://www.makersmakingchange.com/project/lipsync-switch-input-module/ | Page 2 of 3

## Device Setup

If this is a new LipSync: The LipSync has its own set up process that must be referred to first. The LipSync start-up guide can be found here: https://github.com/makersmakingchange/LipSync/blob/master/LipSync_Startup_Guide.pdf

Once the LipSync has been calibrated and setup, the switch module setup can now begin:

1) Insert the male end of the breakout cable into the female end of the Switched LipSync Modification cable.
2) Insert the first assistive switch into the ‘Left Click’ connector of the breakout cable labelled “TIP”. This female cable end is usually black or white.
3) Insert the second assistive switch into the ‘Right Click’ connector of the breakout cable labelled “RING”. This female cable end is usually red.

## USER QUICK GUIDE

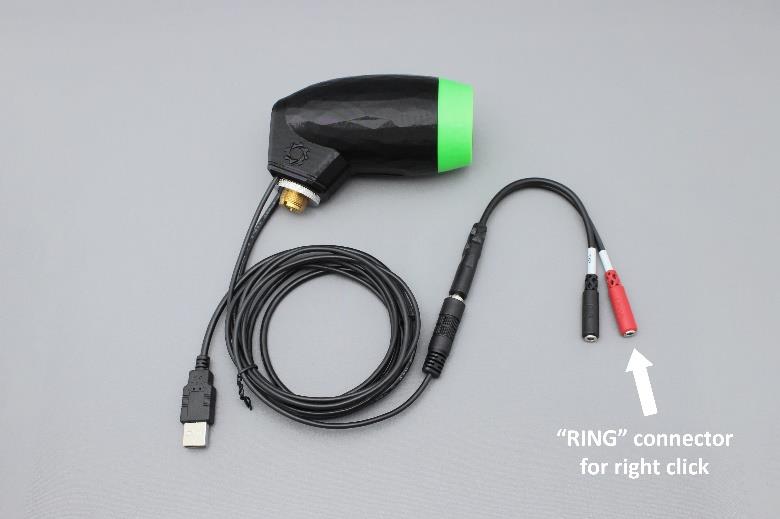
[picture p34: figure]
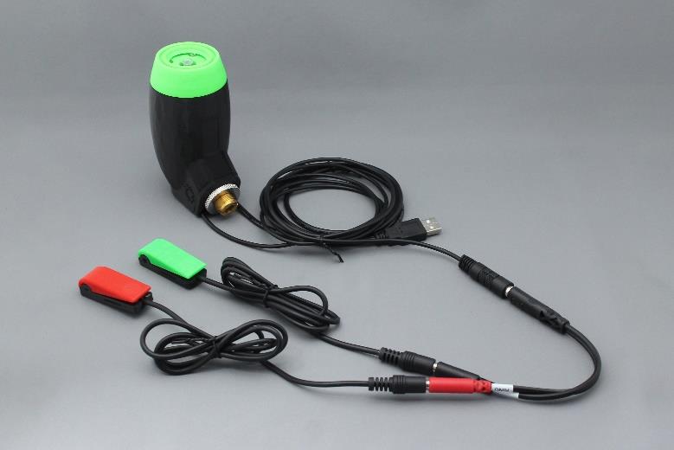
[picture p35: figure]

Files available at https://www.makersmakingchange.com/project/lipsync-switch-input-module/ | Page 3 of 3
4) The Switched LipSync should look like this with two assistive switches connected:
5) Connect the LipSync to a power source such as an electronic device with a USB adapter or a power bank. Wait for the LipSync to initialize. Wait until the LED stops flashing before moving the mouthpiece. Initialization will occur every time the LipSync is powered.

## Specifications

Mass: Approx. 25 grams (Switch Input module with cable, without adaptor cable or switches).

Dimensions: 25 x 27 x 11 mm

## Cleaning

Only the cable will need to be cleaned periodically, as the Switch Module resides internally within the LipSync, and should not normally require cleaning. However, both the cable and module are cleanable with 90% purity (or greater) isopropyl alcohol.

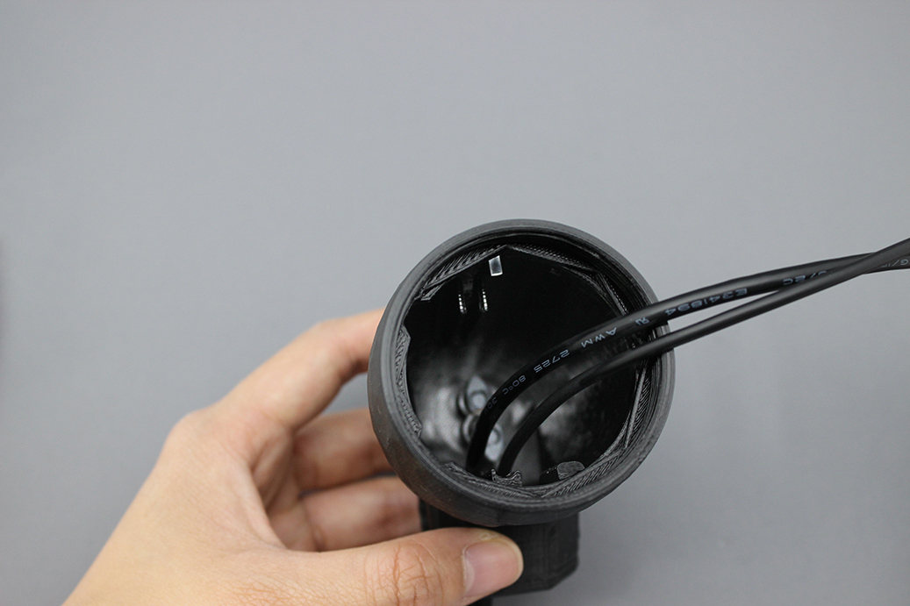
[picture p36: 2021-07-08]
Documentation/Working_Documents/Assembly Images/IMG_1987.jpg

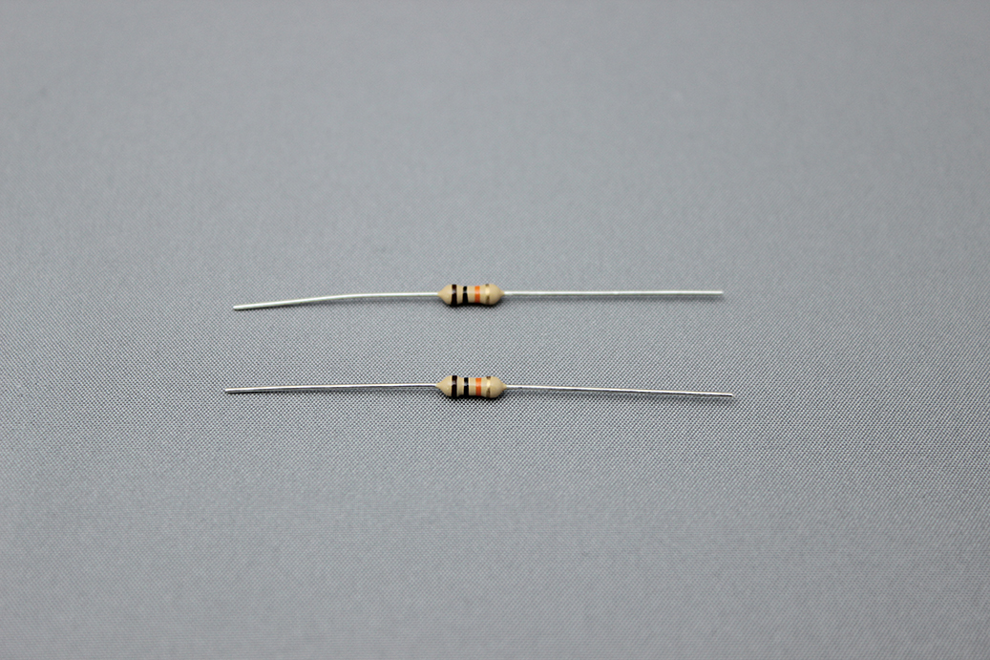
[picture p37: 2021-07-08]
Documentation/Working_Documents/Assembly Images/IMG_0840.jpg

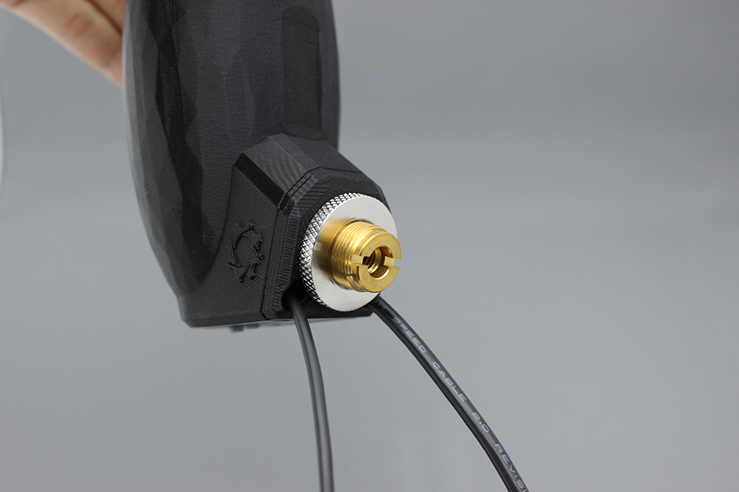
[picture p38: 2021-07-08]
Documentation/Working_Documents/Assembly Images/IMG_2047.jpg

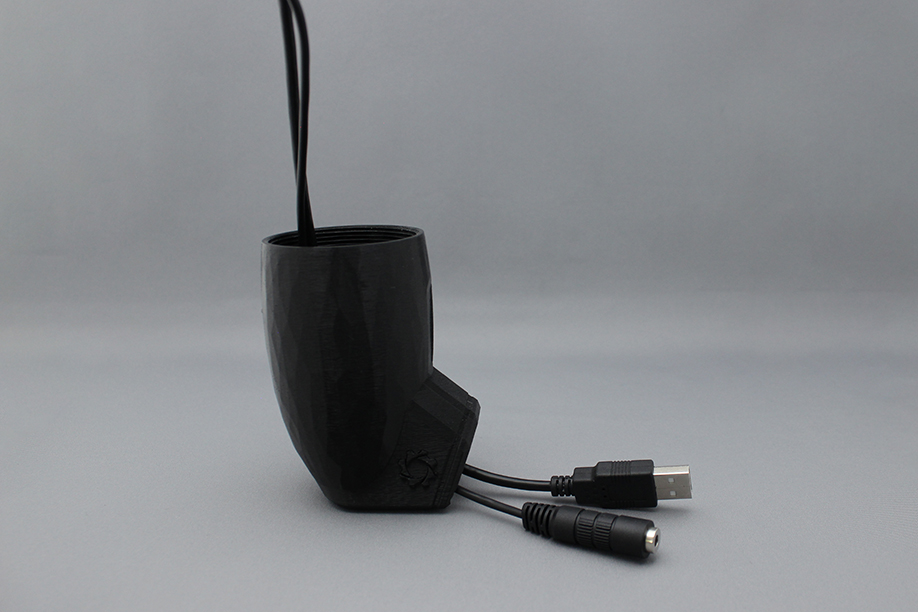
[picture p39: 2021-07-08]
Documentation/Working_Documents/Assembly Images/IMG_1976.jpg

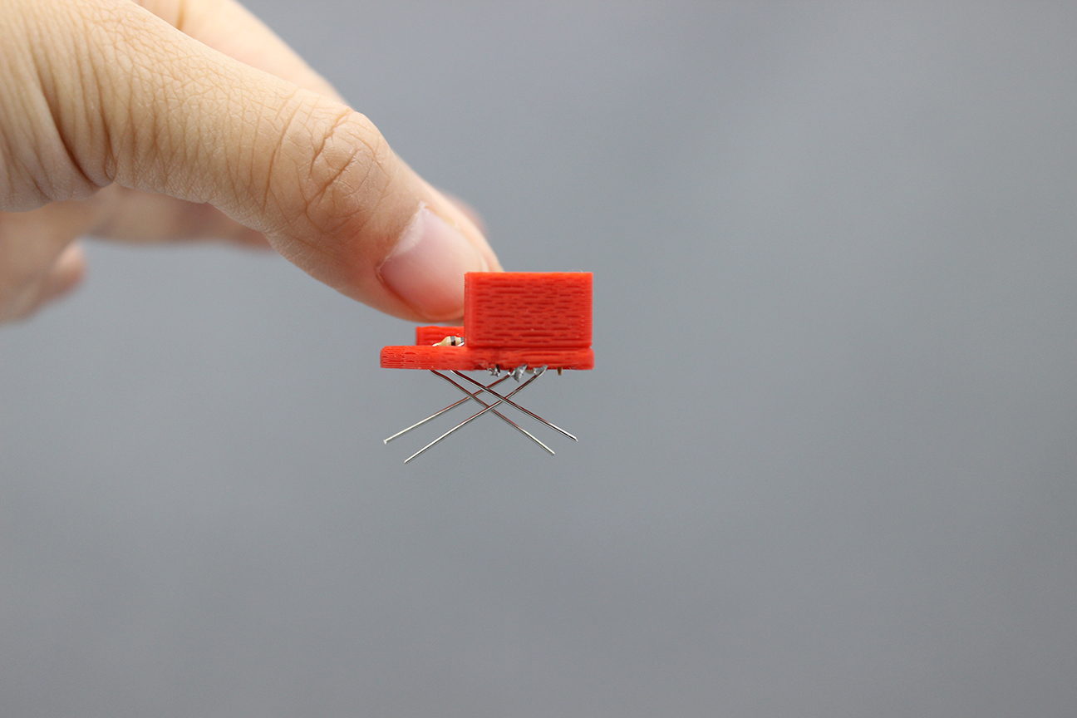
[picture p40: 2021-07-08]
Documentation/Working_Documents/Assembly Images/IMG_0926.jpg

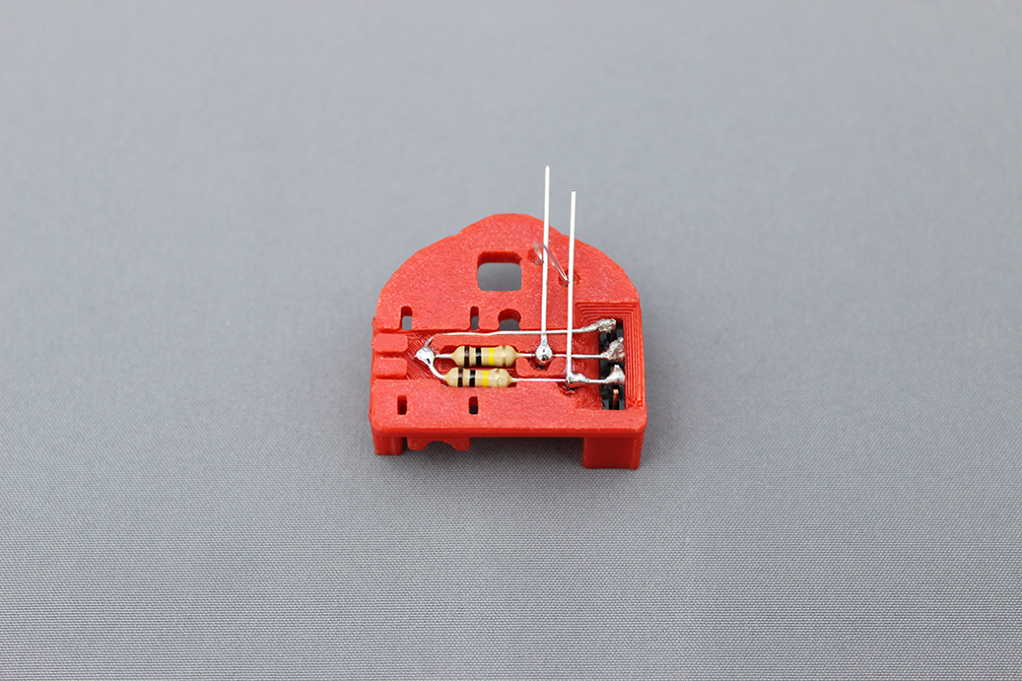
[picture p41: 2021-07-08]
Documentation/Working_Documents/Assembly Images/IMG_1160.jpg

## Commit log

2021-06-04 Create Switch_Input_Module.scad
    Add Eagle file for schematic.
    [Switch_Input_Module.scad]
2021-07-08 Add assembly images
2021-07-08 Add OpenSCAD design file
    [Switch_Input_Module.scad]
2021-07-08 Add initial documentation
    [Switch_Input_Module_BOM.xlsx]
2021-07-08 Rename 3D printing file
    [Switch_Input_3DPCB.stl]
2021-07-08 Update Design Rationale
    Update with breakout cable information.
2021-09-14 Create LipSync_Rear_Housing.STL
    Rear housing that is compatible with Switch Input Module .
    [LipSync_Rear_Housing.STL]
